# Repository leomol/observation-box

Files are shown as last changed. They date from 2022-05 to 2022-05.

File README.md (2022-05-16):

# Observation box for mice

Stackable boxes for observing animal behavior with individual lighting and removable floor and lid.

Inner dimensions are 40 x 15 x 20 cm (approx. 15 3/4 x 7 3/4 x 6")

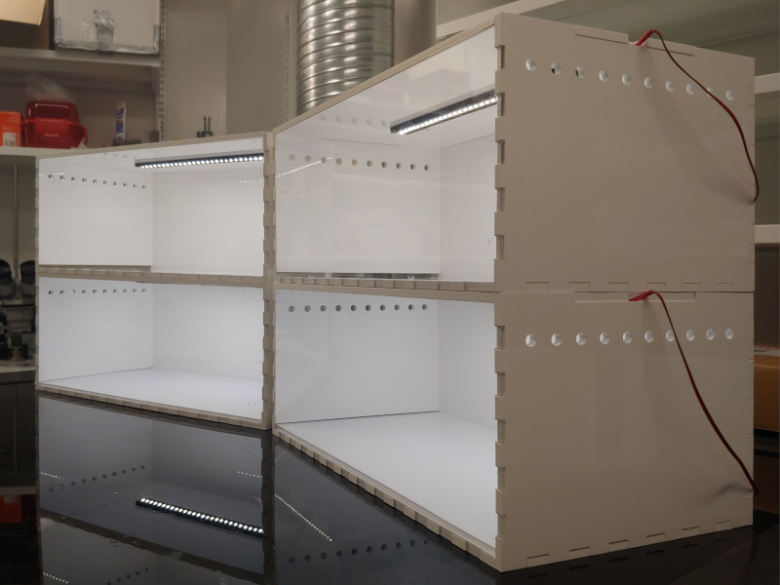
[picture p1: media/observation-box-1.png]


## Components
- [6mm opaque white acrylic sheets](https://www.polymershapes.com/product/acrylic/)
- [3mm clear acrylic sheets](https://www.polymershapes.com/product/acrylic/)
- [4mm corrugated plastic sheets](https://www.polymershapes.com/product/polypropylene-twinwall-corrugated-plastic/)
- [Strip of 30+ LEDs](https://www.digikey.ca/en/products/detail/inspired-led-llc/12V-MB-PW-12M/5866486)
- [LED connector](https://www.digikey.ca/en/products/detail/inspired-led-llc/3496/5866456)
- [Power supply](https://www.digikey.ca/en/products/detail/sl-power-electronics-manufacture-of-condor-ault-brands/ME30A1203F01/5400157)
- [Female DC barrel jack adapter](https://www.digikey.ca/en/products/detail/sparkfun-electronics/PRT-10288/6163697)
- [Power cord](https://www.digikey.ca/en/products/detail/cui-devices/AC-C13-JP/3479178)
- Two-wire cable

## Build instructions
- 3D print the LED holder using the [provided CAD model](CAD). Remove print supports.
- Laser cut the acrylic sheets using the [provided CAD drawings](CAD). Remove protective film.
- Finish cutting the corrugated plastic with the help of a utility knife, if needed.
- Peel the adhesive backing from the LED connector and attach it to the wide space of the LED holder, with the screw terminals facing out.
- Peel the adhesive backing from the LED strip; connect the LED strip to the LED connector -making sure to match the polarity and attach it to the narrow space of the LED holder.
- Connect positive and negative sides of the LED connector to the positive and negative sides of the DC adapter (respectively). Optionally, add a 50 to 200 Ohm resistor in series with one of the two LED cables to dim the lights.
- Assemble all acrylic parts (except for the roof) using painter's tape and apply acrylic cement or 2-part epoxy. Remove painter's tape after drying.
- Use Cyanoacrylate to attach the LED setup to the removable lid.

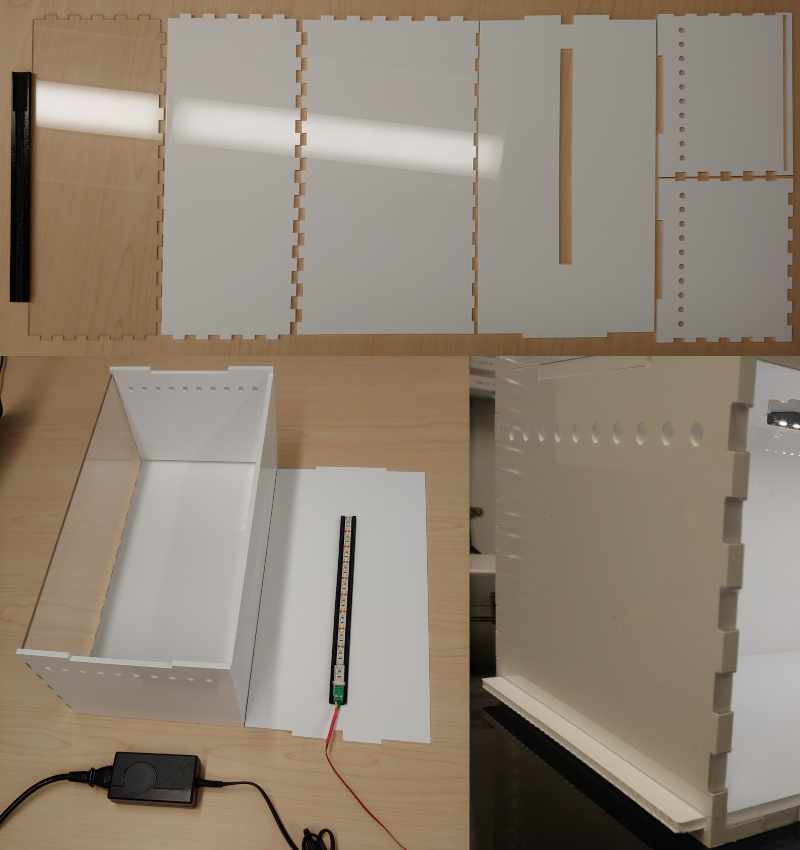
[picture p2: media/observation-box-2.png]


## Usage
- Insert the removable floor made of corrugated plastic.
- Place the mouse in the cage.
- Close the lid and power on the LEDs.

## Version History
### 0.1.0
* 2022-05-13
  - Initial Release.

## License
© 2022 [Leonardo Molina][Leonardo Molina]

This project is licensed under the [Creative Commons BY-NC-SA 4.0 License](https://creativecommons.org/licenses/by-nc-sa/4.0/).

[Leonardo Molina]: https://github.com/leomol
[LICENSE.md]: LICENSE.md

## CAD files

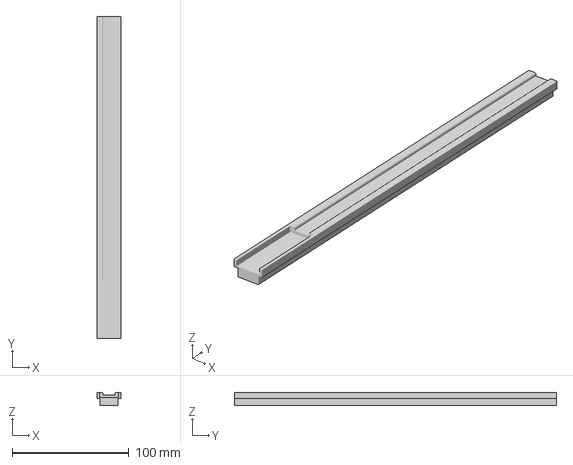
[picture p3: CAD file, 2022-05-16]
CAD/observation-box.3mf
20.5 x 276.0 x 10.8 mm
